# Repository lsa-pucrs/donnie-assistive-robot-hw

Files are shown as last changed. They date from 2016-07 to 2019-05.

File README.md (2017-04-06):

# Donnie's PCB

This repository has all files related to Donnie's hardware (PCB design, schematics, eletrical diagrams, gerber files, BOM files). Donnie has two daugther boards (or 'shields'). One for the Arduino Mega (see ard-shield dir) and the other for the Raspberry Pi (see rasp-shield dir). 

The following image shows Donnie's brain and its electronics.  
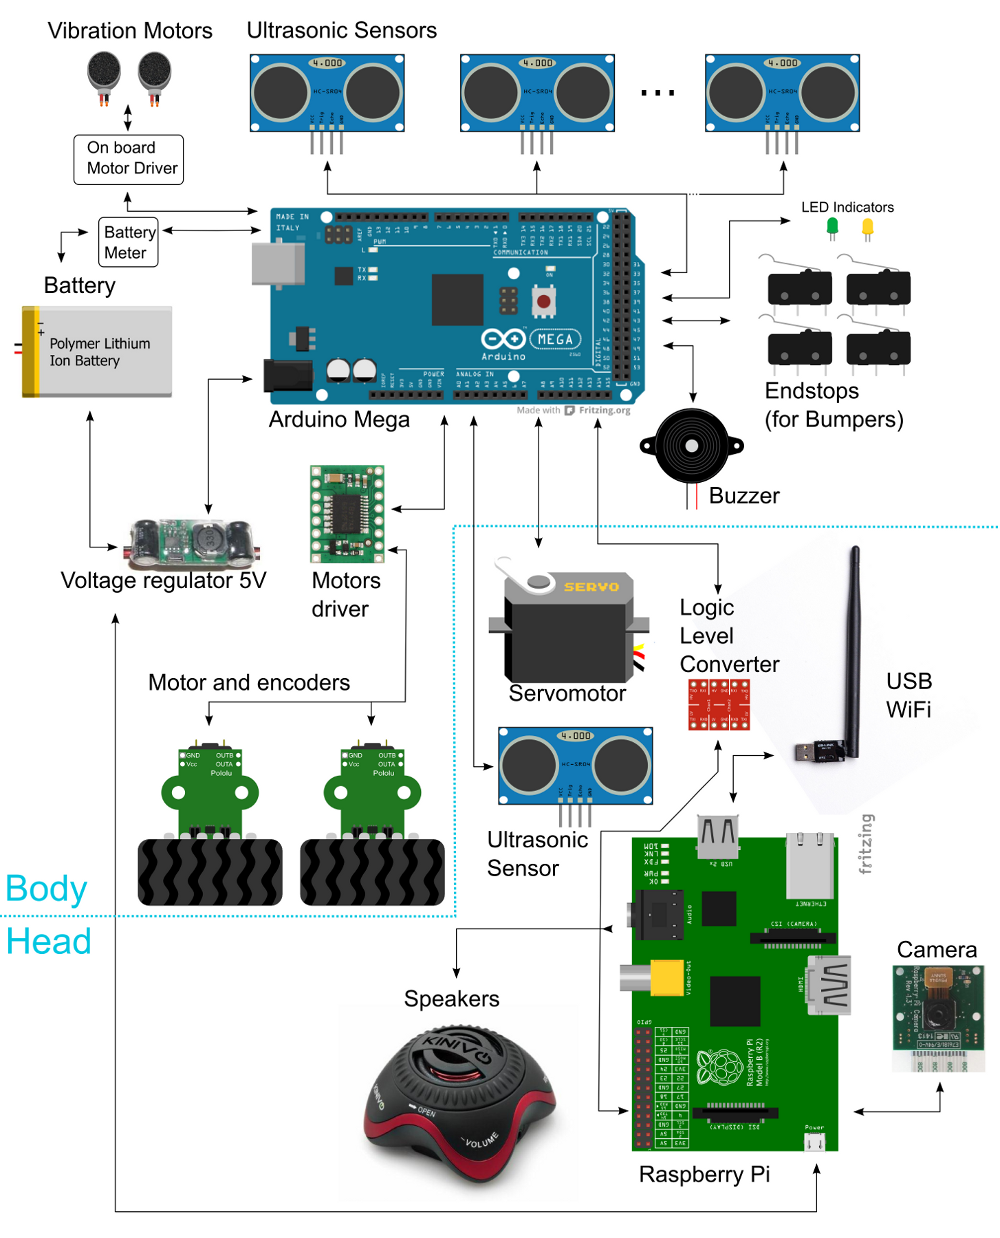
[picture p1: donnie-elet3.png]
Meet Donnie Brain!!!


## Manufacturing the boards

### Send the Gerber for manufacturing

If you just want to manufacture these boards as they are, we recommend the following steps:

 1. Send the Gerber ZIP files ([ard-shield](ard-shield/gerbers/ard_shield-160322-gerbers.zip) and [rasp-shield](rasp-shield/gerber_files/rasp_shield-gerber_files-160118.zip)) to manufacture to Seeedstudio. You should use the following tutorial [Fusion PCB Order Submission Guidelines](http://support.seeedstudio.com/knowledgebase/articles/422482-fusion-pcb-order-submission-guidelines)

### Assembly

 After you receive the PCBs, then follow these steps to assemble the boards:

 1. First of all, separe and buy the components indicated in BOM file ([ard-shield](ard-shield/BOM.txt) and [rasp-shield](rasp-shield/BOM.txt));
 2. Print the PDF schemmatic and BOM file;
 3. Place and weld the componnects in the PCB with the BOM's indicated PART.

## Change the PCB Design

If you want to change the PCB design, we recommend to use Eagle version XYZ.

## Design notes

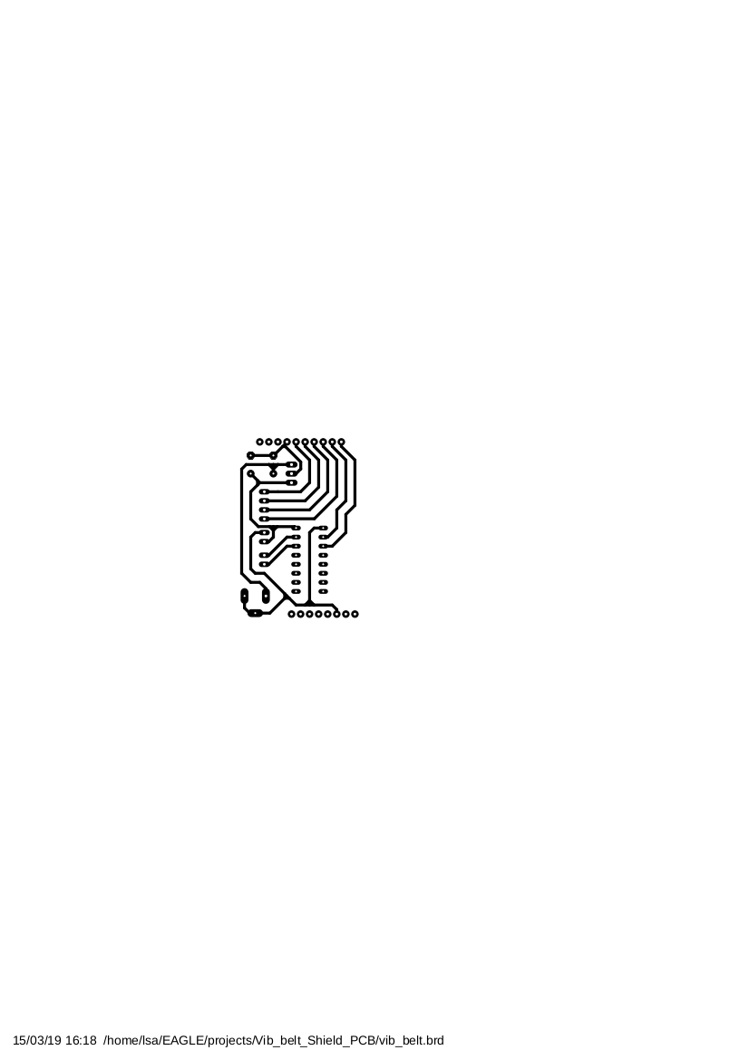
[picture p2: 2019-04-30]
vib-belt/Vib_belt_Nano_PCB/vib_belt.png

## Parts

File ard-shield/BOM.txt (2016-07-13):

Qty Value            Device             Package           Parts

2                    MALE HEADER        1X04              J1, J2-BELOW
6                    MALE HEADER        1X08              J2, 5XARDUINO-MEGA-SHIELD-CONNECTORS
1                    MALE HEADER        1X10              ARDUINO-MEGA-SHIELD-CONNECTORS
1                    MALE HEADER        2X18              ARDUINO-MEGA-SHIELD-CONNECTORS
1                    MALE HEADER        2X05              SDIO
3                    MALE HEADER        1X06              BUMPER, M1, M2
2                    FEMALE HEADER      1X08              U2-HEADER
6                    MALE HEADER        1X04              SONAR1, SONAR2, SONAR3, SONAR4, SONAR5, SONAR6
1                    IC SOCKET          14 PIN            IC2-SOCKET
1                    IC SOCKET          8 PIN             IC1-SOCKET
1                    KRE CONNECTOR      1X3 5MM           X2
3   100 nF           CAPACITOR          POLYESTER 100V    C1, C2, C3
2   1K               RESISTOR           PTH 1/4W          R1, R2
1   1M               RESISTOR           PTH 1/4W          R8
2   33               RESISTOR           PTH 1/4W          R3, R4
2   330              RESISTOR           PTH 1/4W          R5, R6
1   470K             RESISTOR           PTH 1/4W          R7
2   1N4001           DIODO              DO-204AL          D1, D2
2   2N2222A          NPN TRANSISTOR     O92               T1, T2
1   74S32N           OR GATE            DIL14             IC2
1   LM358            OP AMP             DIP08             IC1
1   TB6612           MOTOR DRIVER       MODULE            U2

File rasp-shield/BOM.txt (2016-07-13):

Qty Value               Device              Package       Parts
1                       FEMALE HEADER       2X13          JP1-RASPBERRY-CONNECTOR
1                       MALE HEADER         1X03          SERVO
1                       MALE HEADER         1X04          SONAR
1                       MALE HEADER         1X08          COMM
1                       MALE HEADER         1X02          POWER_B
5   10K                 RESISTOR            PTH 1/4W      R1, R2, R3, R4, R5
1   1K                  RESISTOR            PTH 1/4W      R6
1   2N7000              MOSFET              TO-92         Q1

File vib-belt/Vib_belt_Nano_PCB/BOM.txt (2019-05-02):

Partlist exported from /home/blue_/Iniciação Científica/git/donnie-assistive-robot-hw/vib-belt/Vib_belt_Nano_PCB/vib_belt.sch at 5/2/19 1:39 PM

Part          Value       Device       Package      Description       MF MPN OC_FARNELL OC_NEWARK
ARDUINO_NANO1             ARDUINO_NANO ARDUINO_NANO Arduino Nano V3.0                            
J1            5V          JACK-PLUG0   SPC4077      DC POWER JACK            unknown    unknown  
JP1           Shield Out  PINHD-1X6/90 1X06/90      PIN HEADER                                   
JP2           Source Belt PINHD-1X2/90 1X02/90      PIN HEADER

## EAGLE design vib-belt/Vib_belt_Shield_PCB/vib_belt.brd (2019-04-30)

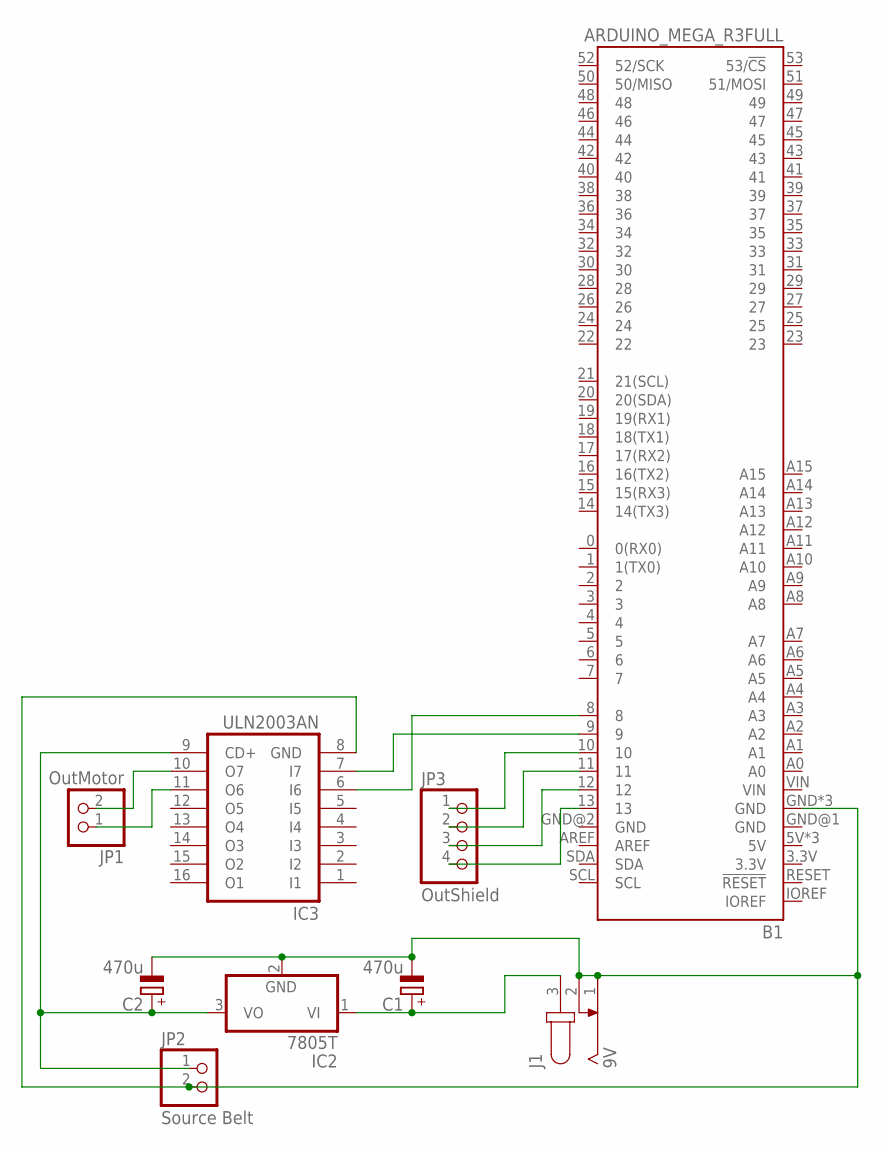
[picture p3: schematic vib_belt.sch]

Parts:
B1: ARDUINO_MEGA_R3FULL; ARDUINO_MEGA_NO_SILK
C1, C2: 470u; E5-6
IC2: 7805T; TO220H
IC3: ULN2003AN; DIL16
J1: 9V; SPC4077
JP1: OutMotor; 1X02/90
JP2: Source Belt; 1X02/90
JP3: OutShield; 1X04/90

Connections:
unnamed: B1.GND, B1.GND@3 (GND), B1.GND@4 (GND), C1.-, C2.-, IC2.2 (GND), IC3.8 (GND), J1.1, J1.2, JP2.2
unnamed: B1.13, JP3.4
unnamed: B1.12, JP3.3
unnamed: B1.11, JP3.2
unnamed: B1.10, JP3.1
unnamed: IC3.10 (O7), JP1.2
unnamed: IC3.11 (O6), JP1.1
unnamed: B1.8, IC3.6 (I6)
unnamed: B1.9, IC3.7 (I7)
unnamed: C1.+, IC2.1 (VI), J1.3
unnamed: C2.+, IC2.3 (VO), IC3.9 (CD+), JP2.1

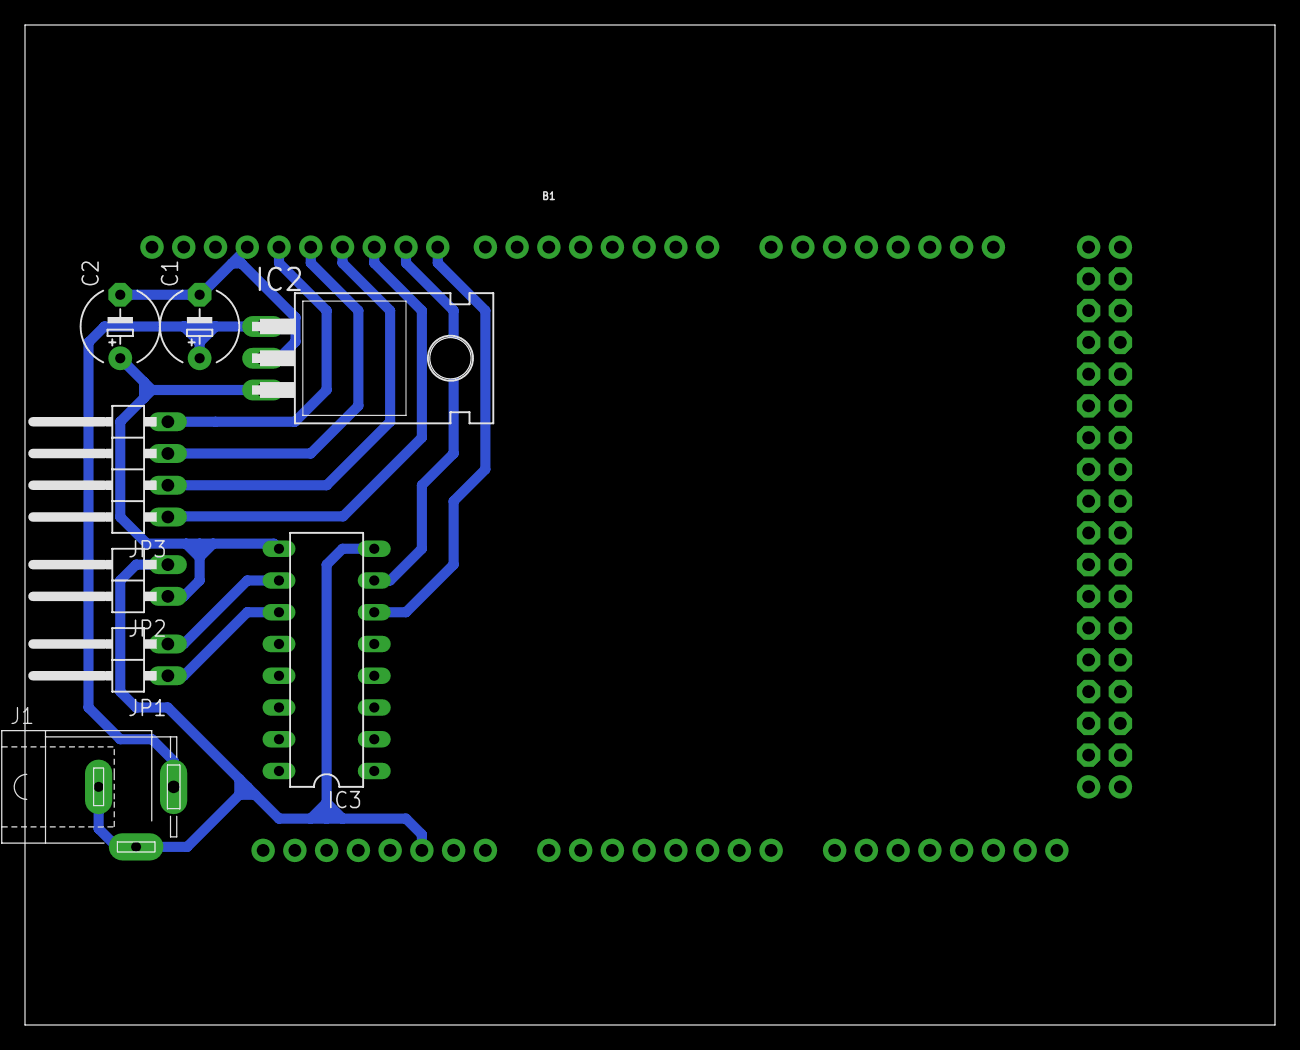
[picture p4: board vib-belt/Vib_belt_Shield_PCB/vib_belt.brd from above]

Board: 2 copper layers, 100.0 x 80.0 mm, 9 parts (0 on the bottom side), 11 nets.

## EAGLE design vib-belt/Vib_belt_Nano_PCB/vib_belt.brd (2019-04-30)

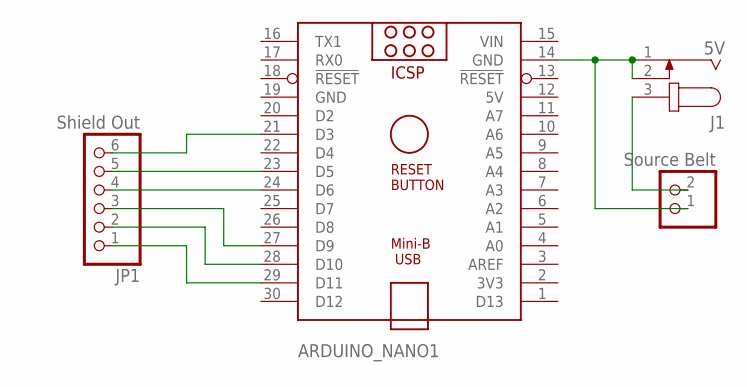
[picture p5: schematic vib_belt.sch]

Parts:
ARDUINO_NANO1: ARDUINO_NANO
J1: 5V; SPC4077
JP1: Shield Out; 1X06/90
JP2: Source Belt; 1X02/90

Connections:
5V: ARDUINO_NANO1.12 (5V)
GND: ARDUINO_NANO1.19 (GND)
unnamed: ARDUINO_NANO1.14 (GND), J1.1, J1.2, JP2.1
unnamed: J1.3, JP2.2
unnamed: ARDUINO_NANO1.29 (D11), JP1.1
unnamed: ARDUINO_NANO1.28 (D10), JP1.2
unnamed: ARDUINO_NANO1.27 (D9), JP1.3
unnamed: ARDUINO_NANO1.24 (D6), JP1.4
unnamed: ARDUINO_NANO1.23 (D5), JP1.5
unnamed: ARDUINO_NANO1.21 (D3), JP1.6
VIN: ARDUINO_NANO1.15 (VIN)

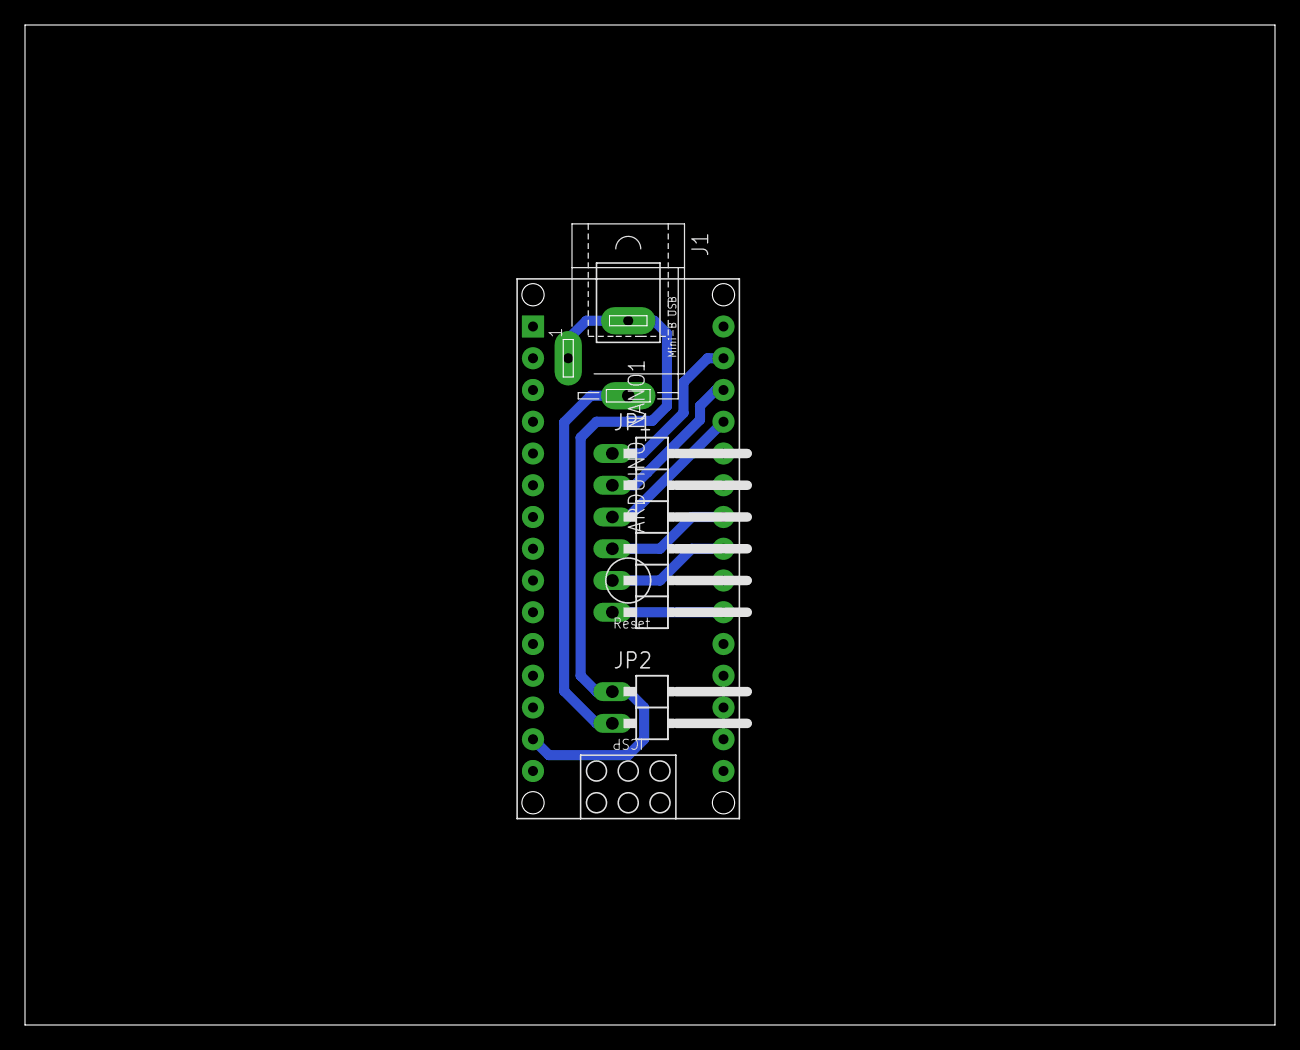
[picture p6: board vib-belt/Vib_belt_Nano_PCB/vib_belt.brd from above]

Board: 2 copper layers, 100.0 x 80.0 mm, 4 parts (0 on the bottom side), 8 nets.

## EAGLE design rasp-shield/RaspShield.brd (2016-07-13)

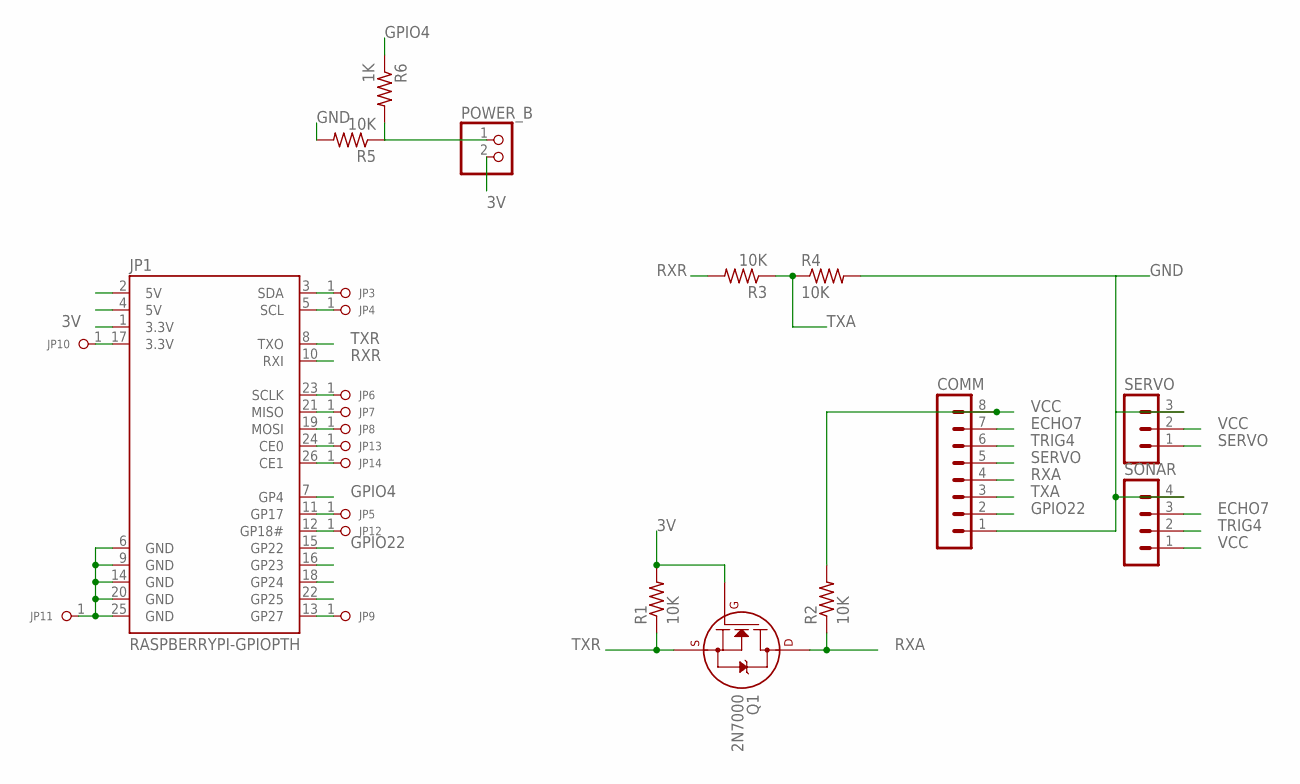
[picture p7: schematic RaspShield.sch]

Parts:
COMM: MA08-1
JP1: RASPBERRYPI-GPIOPTH; 2X13-SHROUDED
JP3, JP4, JP5, JP6, JP7, JP8, JP9, JP10, JP11, JP12, JP13, JP14: PINHD-1X1; 1X01
POWER_B: PINHD-1X2; 1X02
Q1: 2N7000; TO-92
R1, R2, R3, R4, R5: 10K; 0207/7
R6: 1K; 0207/7
SERVO: MA03-1
SONAR: MA04-1

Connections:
3V: JP1.1 (3.3V), POWER_B.2, Q1.2 (G), R1.2
ECHO7: COMM.7, SONAR.3
GND: COMM.1, R4.2, R5.2, SERVO.3, SONAR.4
GP2: JP1.3 (SDA), JP3.1
GP3: JP1.5 (SCL), JP4.1
GP7: JP1.26 (CE1), JP14.1
GP8: JP1.24 (CE0), JP13.1
GP9: JP1.21 (MISO), JP7.1
GP10: JP1.19 (MOSI), JP8.1
GP11: JP1.23 (SCLK), JP6.1
GP17: JP1.11 (GP17), JP5.1
GP18: JP1.12 (GP18#), JP12.1
GP23: JP1.16 (GP23)
GP24: JP1.18 (GP24)
GP25: JP1.22 (GP25)
GP27: JP1.13 (GP27), JP9.1
GPIO4: JP1.7 (GP4), R6.1
GPIO22: COMM.2, JP1.15 (GP22)
unnamed: JP1.17 (3.3V), JP10.1
unnamed: POWER_B.1, R5.1, R6.2
unnamed: JP1.6 (GND), JP1.9 (GND), JP1.14 (GND), JP1.20 (GND), JP1.25 (GND), JP11.1
RXA: COMM.4, Q1.3 (D), R2.1
RXR: JP1.10 (RXI), R3.2
SERVO: COMM.5, SERVO.1
TRIG4: COMM.6, SONAR.2
TXA: COMM.3, R3.1, R4.1
TXR: JP1.8 (TXO), Q1.1 (S), R1.1
VCC: COMM.8, R2.2, SERVO.2, SONAR.1

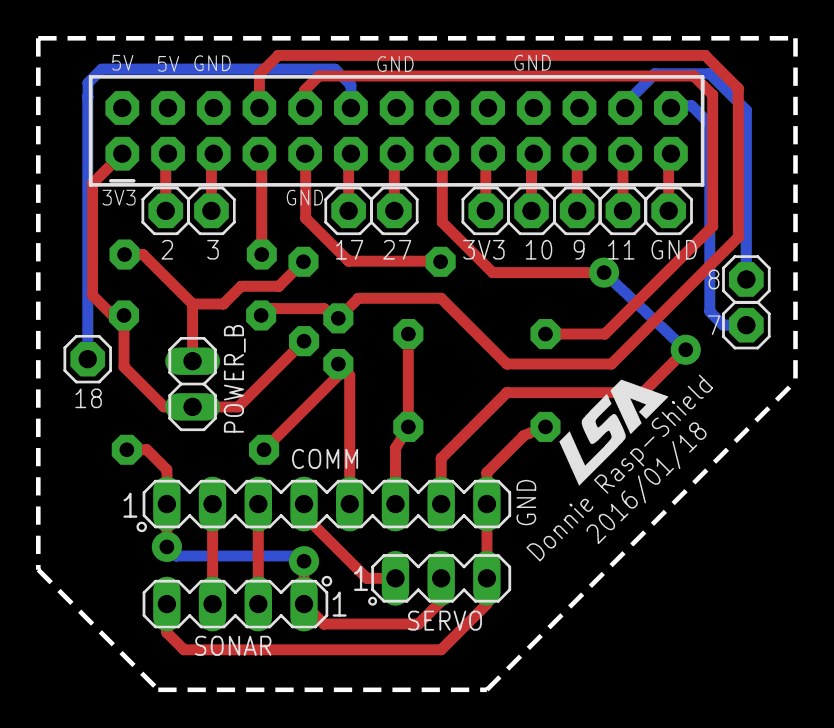
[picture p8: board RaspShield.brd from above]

Board: 2 copper layers, 42.1 x 36.2 mm, 24 parts (1 on the bottom side), 25 nets.

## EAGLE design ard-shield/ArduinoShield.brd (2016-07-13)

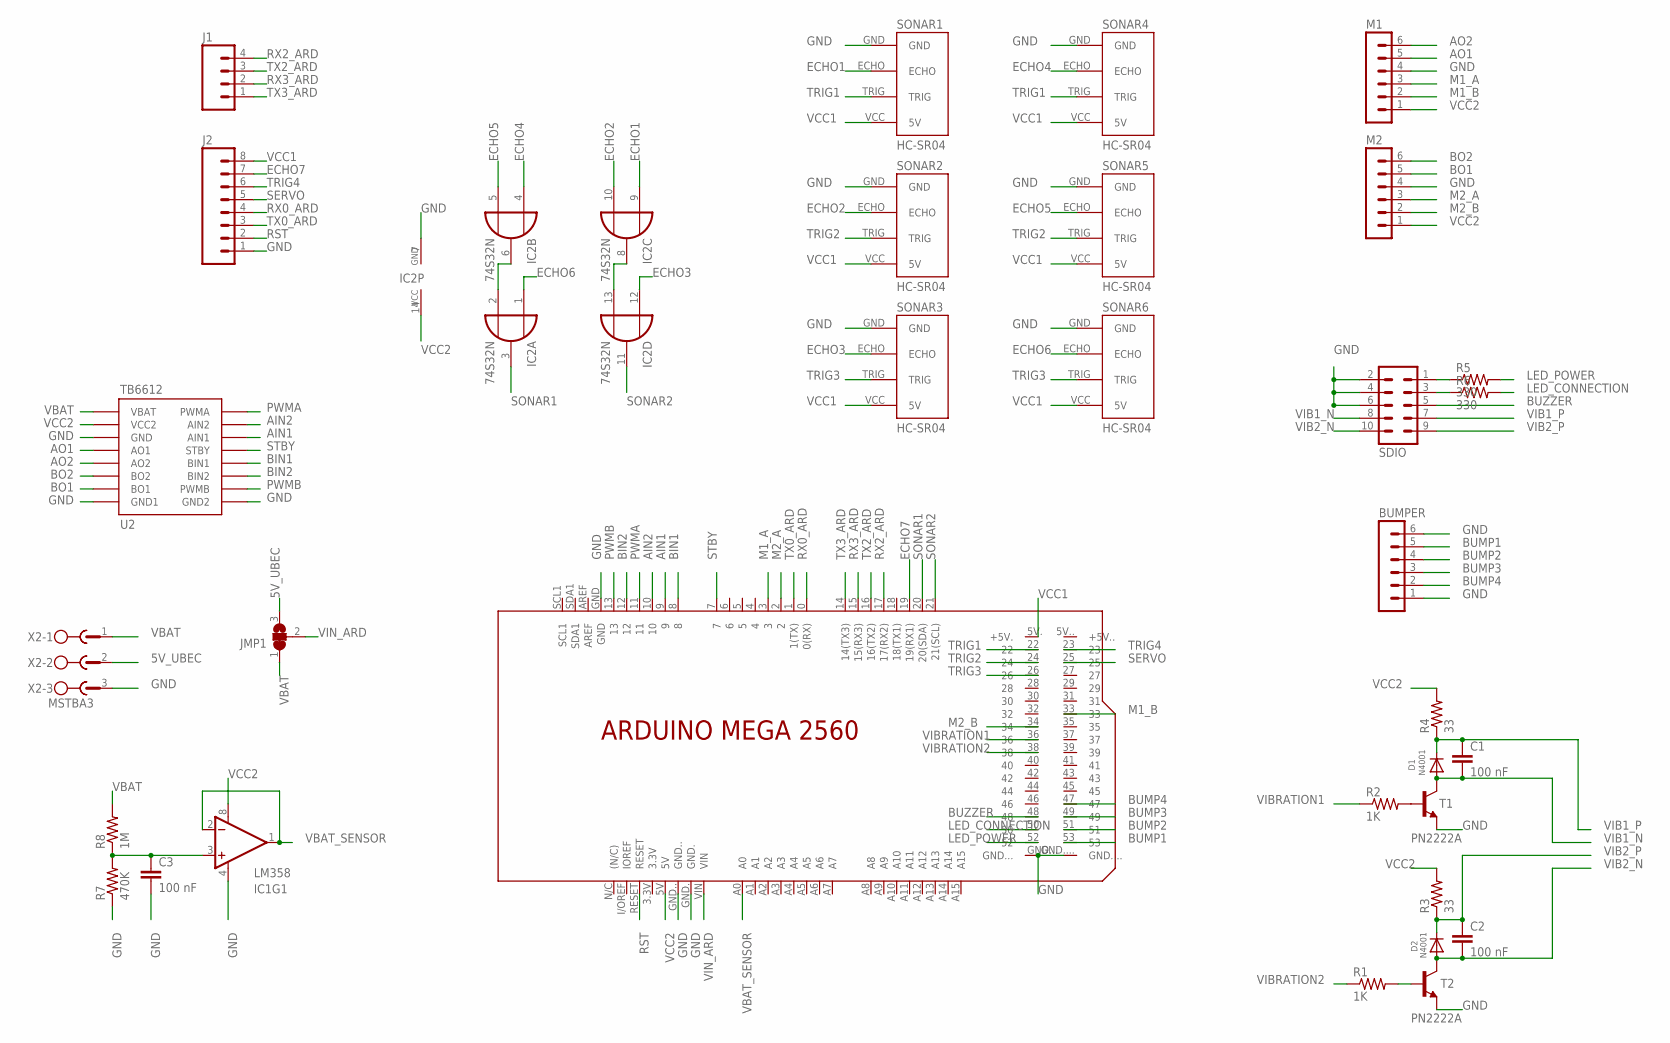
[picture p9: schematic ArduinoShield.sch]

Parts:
BUMPER: MA06-1
C1, C2, C3: 100 nF; C5B2.5
D1, D2: N4001; DO-1N4148
IC1: LM358; DIP08
IC2: 74S32N; DIL14
J1: M04PTH; 1X04
J2: M08SILK_FEMALE_PTH; 1X08
JMP1: SJ2W; SJ_2
M1, M2: MA06-1
PCB1: ARDUINO_MEGA2560
R1, R2: 1K; 0207/2V
R3, R4: 33; 0207/2V
R5, R6: 330; 0207/2V
R7: 470K; 0207/2V
R8: 1M; 0207/2V
SDIO: MA05-2
SONAR1, SONAR2, SONAR3, SONAR4, SONAR5, SONAR6: HC-SR04; HC-SR04_FOOTPRINT
T1, T2: PN2222A; TO92-EBC-OVAL
U2: TB6612
X2: MSTBA3

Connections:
5V_UBEC: JMP1.3, X2.2
AIN1: PCB1.9, U2.P$14 (AIN1)
AIN2: PCB1.10, U2.P$15 (AIN2)
AO1: M1.5, U2.P$4 (AO1)
AO2: M1.6, U2.P$5 (AO2)
BIN1: PCB1.8, U2.P$12 (BIN1)
BIN2: PCB1.12, U2.P$11 (BIN2)
BO1: M2.5, U2.P$7 (BO1)
BO2: M2.6, U2.P$6 (BO2)
BUMP1: BUMPER.5, PCB1.53
BUMP2: BUMPER.4, PCB1.51
BUMP3: BUMPER.3, PCB1.49
BUMP4: BUMPER.2, PCB1.47
BUZZER: PCB1.48, SDIO.5
ECHO1: IC2.9 (I0), SONAR1.ECHO
ECHO2: IC2.10 (I1), SONAR2.ECHO
ECHO3: IC2.12 (I0), SONAR3.ECHO
ECHO4: IC2.4 (I0), SONAR4.ECHO
ECHO5: IC2.5 (I1), SONAR5.ECHO
ECHO6: IC2.1 (I0), SONAR6.ECHO
ECHO7: J2.7, PCB1.19 (19(RX1))
GND: BUMPER.1, BUMPER.6, C3.2, IC1.4 (V-), IC2.7 (GND), J2.1, M1.4, M2.4, PCB1.GND, PCB1.GND., PCB1.GND.., PCB1.GND..., PCB1.GND...., R7.1, SDIO.2, SDIO.4, SDIO.6, SONAR1.GND, SONAR2.GND, SONAR3.GND, SONAR4.GND, SONAR5.GND, SONAR6.GND, T1.E, T2.E, U2.P$3 (GND), U2.P$8 (GND1), U2.P$9 (GND2), X2.3
LED_CONNECTION: PCB1.50, R6.2
LED_POWER: PCB1.52, R5.2
M1_A: M1.3, PCB1.3
M1_B: M1.2, PCB1.33
M2_A: M2.3, PCB1.2
M2_B: M2.2, PCB1.34
unnamed: R2.2, T1.B
unnamed: IC2.2 (I1), IC2.6 (O)
unnamed: R1.2, T2.B
unnamed: IC2.8 (O), IC2.13 (I1)
unnamed: R5.1, SDIO.1
unnamed: R6.1, SDIO.3
unnamed: C3.1, IC1.3 (+IN), R7.2, R8.1
PWMA: PCB1.11, U2.P$16 (PWMA)
PWMB: PCB1.13, U2.P$10 (PWMB)
RST: J2.2, PCB1.RESET
RX0_ARD: J2.4, PCB1.0 (0(RX))
RX2_ARD: J1.4, PCB1.17 (17(RX2))
RX3_ARD: J1.2, PCB1.15 (15(RX3))
SERVO: J2.5, PCB1.25
SONAR1: IC2.3 (O), PCB1.20 (20(SDA))
SONAR2: IC2.11 (O), PCB1.21 (21(SCL))
STBY: PCB1.7, U2.P$13 (STBY)
TRIG1: PCB1.22, SONAR1.TRIG, SONAR4.TRIG
TRIG2: PCB1.24, SONAR2.TRIG, SONAR5.TRIG
TRIG3: PCB1.26, SONAR3.TRIG, SONAR6.TRIG
TRIG4: J2.6, PCB1.23
TX0_ARD: J2.3, PCB1.1 (1(TX))
TX2_ARD: J1.3, PCB1.16 (16(TX2))
TX3_ARD: J1.1, PCB1.14 (14(TX3))
VBAT: JMP1.1, R8.2, U2.P$1 (VBAT), X2.1
VBAT_SENSOR: IC1.1 (OUT), IC1.2 (-IN), PCB1.A0
VCC1: J2.8, PCB1.5V. (+5V.), SONAR1.VCC (5V), SONAR2.VCC (5V), SONAR3.VCC (5V), SONAR4.VCC (5V), SONAR5.VCC (5V), SONAR6.VCC (5V)
VCC2: IC1.8 (V+), IC2.14 (VCC), M1.1, M2.1, PCB1.5V, R3.2, R4.2, U2.P$2 (VCC2)
VIB1_N: C1.2, D1.A, SDIO.8, T1.C
VIB1_P: C1.1, D1.C, R4.1, SDIO.7
VIB2_N: C2.2, D2.A, SDIO.10, T2.C
VIB2_P: C2.1, D2.C, R3.1, SDIO.9
VIBRATION1: PCB1.36, R2.1
VIBRATION2: PCB1.38, R1.1
VIN_ARD: JMP1.2, PCB1.VIN

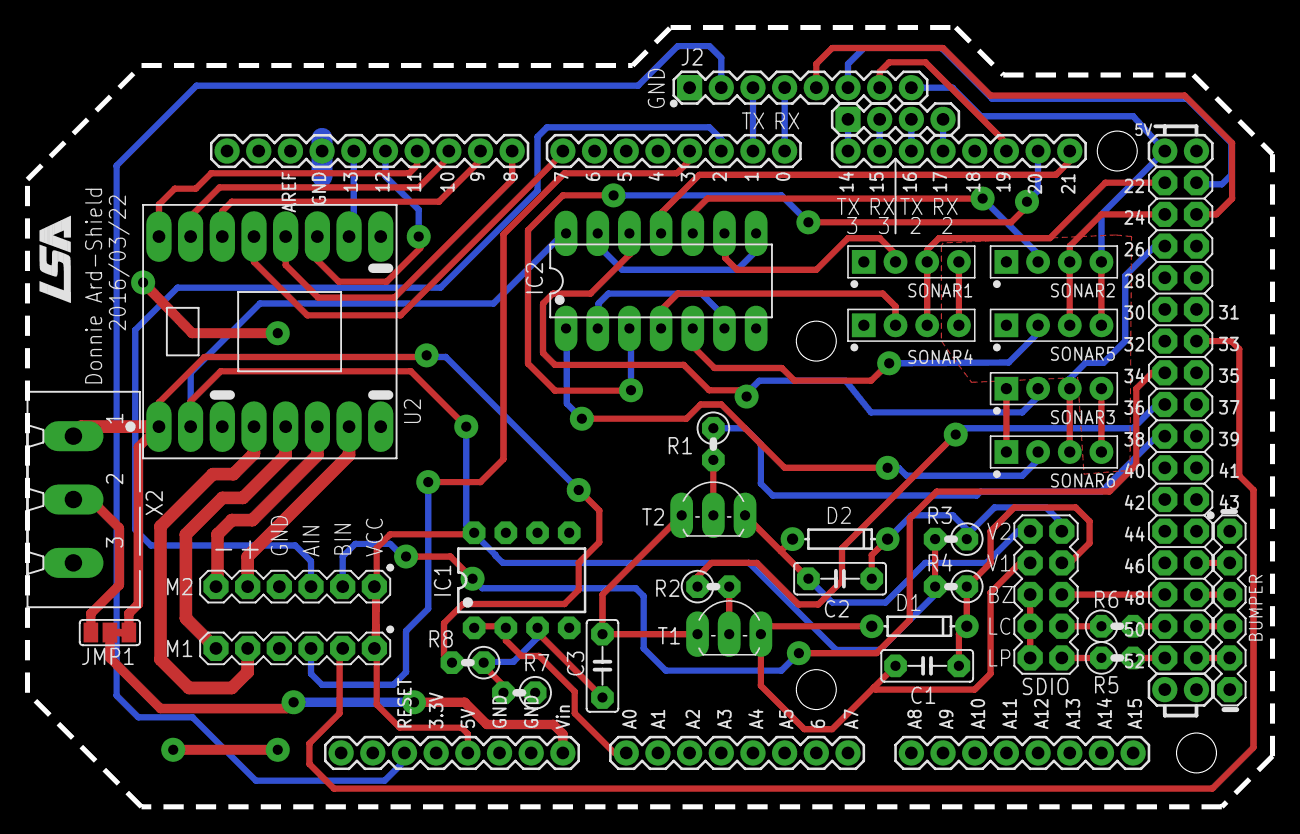
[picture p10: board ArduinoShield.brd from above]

Board: 2 copper layers, 99.8 x 62.5 mm, 33 parts (0 on the bottom side), 63 nets.

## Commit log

2016-07-13 added files of first boards manufactured
    [ArduinoShield.brd, ArduinoShield.sch, RaspShield.brd, RaspShield.sch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]
2016-08-18 updating readme.md
    improved instructions to build the PCBs
2019-04-30 including vib-belt schematics done by Igor
    [vib_belt.brd, vib_belt.sch, vib_belt_ci.fzz]
2019-05-09 Including vib-belt schematics for use with Nano
    [vib_belt_nano.fzz]

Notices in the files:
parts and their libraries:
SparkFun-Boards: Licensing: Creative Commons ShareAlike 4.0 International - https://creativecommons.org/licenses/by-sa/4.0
